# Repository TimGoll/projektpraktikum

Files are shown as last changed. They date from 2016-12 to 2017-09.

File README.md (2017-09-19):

# Dokumentation des Projektpraktikums
Projektpraktikum (Mikrocontrollerpraktikum + Messtechnikpraktikum) Winter- + Sommersemester 2016/17 am LMT

_Tim Goll, Matthias Baltes, Matthias Jost, Markus Herrmann-Wicklmayr_

## Aktuelle Demonstrationsvideos:
[Demovideo 1 (03.12.2016)](https://www.youtube.com/watch?v=2sz4_vMzZEc) <br>
[Demovideo 2 (04.06.2017)](https://www.youtube.com/watch?v=daKc67VaTdY)

## Verwendete Bibliotheken:
1. [**mThread**](http://www.kwartzlab.ca/2010/09/arduino-multi-threading-librar/): <br>
 Erstellt Pseudothreads auf dem Board, die nacheinander ausgeführt werden. Jeder Thread hat seine eigene ```loop()```. <br>
 Threads werden hinzugefügt mittels ```main_thread_list -> add_thread(CLASSNAME)```, anschließend laufen sie unbegrenzt weiter. **Hinweis:** Es sind anscheinend maximal 10 Threads möglich.

2. [**newdel**](https://github.com/jlamothe/newdel): <br>
 Fügt die Keywörter ```new``` und ```delete``` hinzu. Wird für mThread benötigt und musste leicht angepasst werden, damit sie auf neueren Arduino-Boards funktioniert.

3. [**QueueList**](http://playground.arduino.cc/Code/QueueList): <br>
 Fügt verkettete Listen hinzu, welche beliebige Datentypen speichern können. **Hinweis:** Es ist nicht möglich Pointer in ihnen zu speichern.

4. [**Adafruit BME280**](https://github.com/adafruit/Adafruit_BME280_Library) und [**Adafruit Sensor**](https://github.com/adafruit/Adafruit_Sensor): <br>
  Ansteuerung des Boschsensors (Die Version im Repo ist leicht verändert).

## Programmablauf:
1. Programm startet automatisch nach Herstellung der Stromversorgung.
2. Es kann ein Programm per USB von LabView übertragen werden, oder - falls eine SD-Karte eingesteckt ist - ein Programm von der SD-Karte aus gestartet werden.
3. Programm liest Daten (werden überprüft) und startet nach einem Tasterdruck/"Start"-Befehl.
4. Arbeitet Eventlisten ab, gibt Debug-Informationen aus, sofern über Schalter aktiviert, während der Laufzeit einstellbar.
5. Im Idle-Modus nach vollständiger Abarbeitung aller Events; nach Abschluss des Programms leuchtet eine LED und das Display leuchtet grün.
6. Zum Starten eines weiteren Programms muss das Board zurückgesetzt werden.
7. Es sind maximal 14.000 Events auf dem Board möglich. Dann ist der Speicher voll.
8. Für eine korrekte Steuerung muss **mindestens ein Ventil und ein MFC** existieren, sonst kommt es zu Fehlern. Falls in der Steuerung kein MFC/Ventil gebraucht wird, kann man auch einen leeres pseudo MFC/Ventil hinzufügen, das keine Events hat. Dafür muss nicht einmal Hardware angeschlossen sein.

## Übertragungsprotokoll (LabView -> Mikrocontroller):
Die Übertragung erfolgt zeilenweise in einem möglichst übertragungssicheren Format. Als Anfangs- und Endzeichen dienen zur Überprüfung der Vollständigkeit jeweils eine öffnende und eine schließende spitze Klammer. Alle Zeitangaben sind in Millisekunden. Es gibt nur ganzzahlige Integerwerte.

Die IDs der MFCs und Ventile ergeben sich jeweils aus der gegebenen Reihenfolge startend bei null.

**Zeilenweise Betrachtung der Übertragung**:

1. ```<Anzahl MFC, Anzahl Ventile>```
2. ```<Adresse MFC 0, Adresse MFC 1, ...>```
3. ```<Typ MFC 0, Typ MFC 1, ...>```
4. ```<Ventilplatinenadresse1, ...>``` Hexadezimale Ventilplatinenadressen
5. ```<Platinen-ID Ventil-Pin-ID, Platinen-ID Ventil-Pin-ID, ...>```
6. ```<Messintervall>``` Mess- und Speicherintervall in Millisekunden
7. ```<Datum + Zeit>``` Aktuelles Datum & Uhrzeit. Wird im Header der Messung gespeichert, relativ dazu wird gemessen
8. ```<begin>``` Ende des Headers, Beginn mit der Eventübertragung
9. ```<MFC oder Ventil, ID, Wert, Zeit>``` Setze Events. Hierbei müssen die Events je MFC/Ventil zeitlich sortiert sein, um eine einfachere Verarbeitung zu gewährleisten. Untereinander dürfen die Events jedoch vertauscht sein. (Zeit von MFC2 darf vor MFC1 sein, auch bei späterer Übertragung. Jedoch darf Zeit von MFC1 nicht vor der Zeit von MFC1 sein)
10. ```<end>``` Ende der Eventübertragung, warte auf Start der Messung
11. ```<start>``` Nicht zwingend notwendig, kann auch manuell per Taster gestartet werden

**Beispiel**:

```
<6,9>
<adresse0,adress1,adresse2,adresse3,adresse4,adresse5>
<typ0,typ1,typ2,typ3,typ4,typ5>
<0x20>
<0 0, 0 1, 0 2, 0 3, 0 4, 0 6, 0 9, 0 12, 0 15>
<10>
<08.02.2017-13:03:29>
<begin>
<M,0,120,1000>
<M,0,240,1500>
<M,1,170,800>
<M,0,150,1700>
...
<V,0,1,1200>
...
<end>
<start>
```

**Softwarereset**: Es ist auch möglich, das Board per Software neu zu starten. Dafür muss ein ```reset``` Befehl übertragen werden, woraufhin das Board neu startet und anschließend wieder ein ```ready``` ausgibt. (Hardwareimplementierung noch ausstehend). Weiteres siehe Ausblick.

## Serielle Kommunikation:
Vier Ports des Boards werden verwendet. Port 0 dient zur Kommunikation mit LabView (IN/OUT), Port 1 gibt Debug-Nachrichten aus, sofern der Debug-Schalter am Board aktiviert ist. Zur Kommunikation mit den MFCs dient Port 2.

Es gibt eine extra Klasse namens ```serialCommunication```, welche die Kommunikation über die vier Ports verwaltet. Zu Beginn muss in der ```setup()```-Funktion der Hauptino das Objekt initialisiert werden:
```cpp
srl->setSerial(&Serial1, &Serial3, &Serial2, &Serial4); //labview / debug / mks / buerkert
```
Anschließend kann man an beliebiger Stelle im Programm diese Klasse einfach nutzen:
```cpp
srl->print('D', "Hallo Welt!"); //(Typ: L, D, M, B / Ausgabetext)
srl->println('D', "Hallo Welt mit Zeilenende!"); //Natuerlich gibt es das ganze auch mit Linebreak
```
Der Typ der Ausgabe entscheidet, welcher Port genutzt wird. Hierbei gibt es drei Typen: L, D und M, B für LabView, Debug, MKS und Bürkert. Die Parameter, wie die Baudrate, werden in der **config.h** eingestellt.

Über den LabView-Port wird nach erfolgreicher Initialisierung des Boards ein _"ready"_ gesendet. Wurde ein Befehl korrekt erkannt und erfolgreich verarbeitet, wird ein _"ok"_ gesendet, andernfalls kommt ein Errorcode. Nach Abschluss einer Messung wird eine _"finished"_ Zeile übertragen.

## Serielle Hardware
Die Verbindung zwischen dem Teensy und dem PC über eine serielle Verbindung wird mit dem IC **CH340G** realisiert. Dieser funktioniert Plug and Play unter Windows (Windows 10 getestet) und lässt sich auch [mit einfachen Treibern](https://github.com/adrianmihalko/ch340g-ch34g-ch34x-mac-os-x-driver) unter MacOS zum Laufen bringen.

## SD Karte
Das SD-System des Teensy basiert auf FAT, daher sind Dateinamen maximal acht Zeichen lang (Großbuchstaben). Dateinamen, die länger als diese acht Zeichen sind, werden automatisch gekürzt (8.3 Format). Beim Speichern in eine Datei ist es jedoch wichtig, dass der Dateiname maximal 8 Zeichen hat, ansonsten tritt ein Fehler auf.

Die SD-Karte wird nur einmal beim Programmstart initialisiert. Es ist also nicht möglich, sie während der Laufzeit einzustecken oder zu entfernen. Ersteres wird nicht erkannt, letzteres führt zu Datenverlust. Wenn eine SD-Karte beim Programmstart erkannt wird, so wird dies durch ein Zeichen in der linken oberen Ecke gezeigt.

Eine neue SD-Karte kann einfach in den Leseslot gesteckt werden, alle nötigen Verzeichnisse werden automatisch erstellt. (Board muss resettet werden!)

### Messergebnisse
**Namensschema:** ```YYMMDDXX```<br>
Datum in Zweierschreibweise, zwei X für eine fortlaufende Nummerierung. Es sind maximal 100 (0..99) Messungen an einem Tag möglich. Falls der Zähler die 100 Überschreitet, werden kontinuierlich Messungen unter der Nummer _"xx"_ abgespeichert und überschrieben.

Beim Speichern auf der SD-Karte wird eine Datei mit einem Dateinamen, der das Datum und die Messungsnummer (falls mehrere Messungen pro Tag) enthält, erzeugt. Im gleichen Zuge wird in der txt-Datei ein Header in Klartext erstellt. Dieser enthält wesentliche Informationen wie die Startuhrzeit (diese stammt aus dem Header des Programms) der Messungen, die Anzahl der MFC's und Ventile, sowie die Typen der MFC's.

#### Beispielmessung
```
Messung am:     17.03.2017-22:12:46
Messintervall:  100
Anzahl Ventile: 6
Anzahl MFCs:    4
Typen der MFCs: MKS MKS MKS MKS

Wertsortierung: Laufzeit (ms), MFC Soll, MFC Ist, Ventil Soll, Bosch (Temp /C, Druck /Pa, Feucht /%)

0   0 0 0 0 0 0 0 0 0 0 0 0 0 0 22.520000 99050.312500 53.992188
100 0 0 0 0 0 0 0 0 0 0 0 0 0 0 22.520000 99050.312500 53.992188
200 0 0 0 0 0 0 0 0 0 0 0 0 0 0 22.520000 99048.062500 54.057617
300 0 0 0 0 0 0 0 0 0 0 0 0 0 0 22.520000 99042.750000 54.057617
.........
```

### Programme
1. Einzelne Befehlzeilen werden mit einem ```\n``` (Zeilenumbruch) voneinander getrennt.
2. Die Befehlszeilen werden bei Dateien **nicht** mit ```<``` und ```>``` umschlossen.
3. Leerzeilen und Leerzeichen werden ignoriert
4. Ebenso wird alles in einer Zeile nach einem ```#``` ignoriert, somit sind Kommentare möglich.
5. Dateinamen sind im FAT 8.3 Format und dürfen nicht mit ```.``` oder ```_``` beginnen.
6. Programme müssen sich im Ordner ```programs``` auf der SD Karte befinden.

#### Beispielprogramm
Nach dem Einstecken einer neuen SD Karte und dem Neustart des Boards wird eine Beispielprogrammdatei auf der SD Karte erstellt, die wie folgt aussieht:

```
# DIES IST EINE BEISPIELDATEI.
# Dateinmane duerfen nicht mit '.' oder '_' beginnen, sonst werden sie ignoriert.
# Im Gegensatz zu einer LabView Uebertragung sind hier Kommentare moeglich.
# leere Zeilen und Leerzeichen werden ignoriert.

4,16 #(MFCs, Ventile) in Dateien werden keine Tags benutzt
01,21,07,14 #(MFC Adressen)
Buerkert,Buerkert,MKS,MKS #(MFC Typen)
0x20 #(Ventilplatinen Adressen)
0 0, 0 1, 0 2, 0 3, 0 4, 0 5, 0 6, 0 7, 0 8, 0 9, 0 10, 0 11, 0 12, 0 13, 0 14, 0 15 #(Ventil Pins)
250 #(Messintervall)
08.02.2017-13:03:29 #(Datumstring)

begin #Ende Header, uebertrage Eventliste

M,0,120,1000
V,0,1,1000
V,1,1,750

end #Uebertragung abgeschlossen
start #Optionaler automatischer Programmstart
```

## I2C
I2C wird als Hauptkommunikationsbus verwendet. Folgende Adressen sind belegt (In der Klammer stehen die alternativen Adressen):
- Display: 0x38 (--)
- BME280: 0x76 (0x77)
- IO Expander (Ventilplatine, PCA9555): 0x20 (0x21 .. 0x27)

## BME280
Der Boschsensor wird innerhalb der Klasse ```main_boschCom``` verwaltet. Dort wird ein bme-Objekt erstellt. Dieses Objekt wird geliefert von einer leicht angepassten Adafruit-Bibliothek. (Diese könnte man noch weiter reduzieren, da der ganze SPI Bereich eigentlich nicht gebraucht wird)

**Anschluss des Sensors:**<br>
Folgende Pinbelegung ergab sich nach einigem Durchmessen mit einem Multimeter. Bisher erwies sich dieses Layout als korrekt.
```
        +----\_/----+
    VDD |o         o|                     VDD und VDDIO   : 3V3
  VDDIO |o         o|                     GND             : 0V
    GND |o         o|                     SDO (Adresspin) : 0V (0x76), 3V3 (0x77)
    SDO |o         o|                     CSB             : 3V3
    SDA |o         o|                     SDA / SCL       : I2C Bus (3V3 level)
    SCL |o         o|
    CSB |o   |_|   o|
        |o         o|
        |o         o|
        |o         o|
        |o         o| (SCL)
        |o         o| (SDA)
        |o         o|
        |o         o|
        |           |
        +-----------+
```
Den Sensor auslesen kann man in der besagten ```main_boschCom``` mit folgenden Befehlen:
```cpp
this->bme280->readTemperature();
this->bme280->readPressure();
this->bme280->readHumidity();
```

## Ventile
Die Ventilsteuerung befindet sich auf einer eigenen Platine. Das hat die beiden Vorteile, dass zum einen Kurzschlüsse auf der Ventilplatine keinen Schaden an der Hauptsteuerung verursachen können und es zum anderen möglich ist, "beliebig" viele Ventile mit einem Mikrocontroller zu steuern.

Theoretisch sind bis zu 8 Ventilplatinen mit je 16 Ventilen möglich, also insgesamt 128 Ventile. Auf der Platine befindet sich ein dreipoliger DIP-Switch zum Einstellen der Adresse (Adressraum: 0x20..0x27). Die Adressen sind bei Programmstart per LabView an den Controller zu übertragen. Jede der acht Platinen hat 16 Pins (0 bis 15), die auch bei der Initialisierung so angegeben werden müssen (```<Platinen-ID Pin-ID, ...>```). Intern haben die Ventile jedoch eine andere, fortlaufende, Nummerierung (siehe Übertragungsprotokoll).

Die softwareseitige Ansteuerung wird mittels einer kleinen von uns geschriebenen Bibliothek namens ```pca9555``` (Name des I2C ICs) realisiert. Angelehnt an die Syntax der Arduino-Umgebung gibt es auch hier eine ```digitalWrite(pinNumber)```-Funktion, der Einfachheit halber haben wir jedoch auf weitere Funktionen verzichtet und bei Porgammstart werden automatisch alle Pins als Ausgang definiert.

## Display:
Das Display ist via I2C mit dem Board verbunden, die Hintergrundbeleuchtung funktioniert mittels drei PWM Anschlüssen, einer für jede Grundfarbe. Daraus können beliebige Hintergrundfarben erzeugt werden. <br>
Je nach Meldungstyp ist die Hintergrundfarbe unterschiedlich. Folgende Typen gibt es:

- **Unkritische Fehler**: Error Code Level 1000; Dies sind Fehler, die beispielsweise bei der Kommunikation auftreten, aber keinen Programmabbruch benötigen. Sie werden auf dem Display für 2 Sekunden angezeigt. Farbe: _orange_
- **Kritische Fehler**: Error Code Level 5000; Diese Fehler führen zu einem Abbruch des Programms und werden auf dem Display angezeigt bis der Fehler behoben wurde. Farbe: _rot_

Standardmäßig werden auf dem Display aktuelle Daten zum Programmstatus angezeigt.

**Beispielanzeige**:
```
STANDARD:                      ERRORBEISPIEL:                 ENDANZEIGE:
+----------------------+       +----------------------+       +----------------------+
|          #M:04 #V:07 |       |      ERROR 1001      |       |          #M:04 #V:07 |
|                      |       |                      |       |                      |
| LAUFZEIT:00:01:34:17 |       |       Falscher       |       |    ABGESCHLOSSEN     |
| V03-0001-00:01:16:22 |       |     Zeilenbeginn     |       |     02:05:24:34      |
+----------------------+       +----------------------+       +----------------------+
Hintergrund: weiß              Hintergrund: organge/rot       Hintergrund: grün
```

- **Standardanzeige:** <br>
 Zeile 1: Anzahl MFCs und Anzahl Ventile <br>
 Zeile 2: xxx <br>
 Zeile 3: Laufzeit der Software, relativ zum Messstart <br>
 Zeile 4: Letztes Event, Typ-ID-Wert-Zeit
- **Erroranzeige:** <br>
 Zeile 1: Error ID <br>
 Zeile 2: xxx <br>
 Zeile 3+4: Kurzbeschreibung des aufgetretenen Fehlers
- **Endanzeige:** <br>
 Zeigt durchgängig diesen Text an, lässt sich nur zurücksetzen durch Reset des Boards

## Errormeldungen:
Bei allen Fehlermeldungen im 1000er Bereich wird das Programm weiterhin ausgeführt, es wird jedoch eine Wiederholung der entsprechenden Zeile erwartet, daher sind diese Codes LabView-seitig abzufangen.

### 1000:
**Maximale Input-String Länge überschritten.** In der _config.h_ wird eine Zeichenanzahl definiert, die pro Zeile gesendet werden darf. Diese Länge darf nicht überschritten werden.

### 1001:
**Falscher Zeilenbeginn.** Die Zeile muss mit einer öffnenden spitzen Klammer ```<``` begonnen werden, damit sie als gültig akzeptiert wird. Dies dient der Vollständigkeitsüberprüfung.

### 1002:
**Falsches Zeilenende.** Die Zeile muss mit einer schließenden spitzen Klammer ```>``` beendet werden, damit sie als gültig akzeptiert wird. Dabei darf man jedoch nicht vergessen, dass die Stringeingabe mit einem Zeilenumbruch ```\n``` als vollständig markiert wird. Dies dient der Vollständigkeitsüberprüfung.

### 1003:
**Lese-Timeout überschritten.** In der _config.h_ wird eine maximale Lesezeit pro String definiert. Wird diese Zeit überschritten, wird das Lesen des Strings an dieser Stelle abgebrochen.

### 1004:
**Falsche Anzahl an Argumenten.** Bei der Übertragung von LabView an den Controller wird immer überprüft, ob die Anzahl an eingetroffenen Elementen der Anzahl an erwarteten Elementen entspricht.

### 5000:
**Zugriff auf nicht definierte MFC/Ventil ID.** Tritt dieser Fall ein, dann wird eine irreversible Errormeldung geworfen, die nur duch einen Programmneustart behoben werden kann. Man sollte in diesem Fall seine Eingaben darauf überprüfen, ob in den Events nur auf vorher definierte MFCs/Ventile zugegriffen wird.

## MFCs
Bei unserem Aufbau verwenden wir zwei verschiedene Typen von MFCs. **Bürkert** und **MKS** sind die beiden Hersteller. Dazu gibt es noch alte analoge MFCs, die von einer anderen Projektgruppe digitalisiert wurden. Diese basieren dadurch auch auf dem **Bürkert** Protokoll. <br>
Von uns angesteuert werden alle MFCs von ihrer jeweiligen Klasse, je nach Typ bekommen sie bei der Initialisierung jedoch ein anderes Kommunikationsobjekt übergeben. Dieses Objekt führt verschiedene Befehle aus und gibt gegebenenfalls Daten an das MFC-Objekt zurück.

Um Verzögerungen zu verringern wird die Übertragung mittels zeitlichen Interrupts gesteuert. Sowohl mfcCom_mks, als auch mfcCom_buerkert besitzen einen ```IntervalTimer```, der mikrosekundengenaue Callbackfunktionen ausführen kann. Zum Start der Befehlsübertragung wird die Übertragungs- und Antwortzeit berechnet, sowie die erwartete Pause zwischen den beiden Übertragungen. Nach dem Schieben des Strings in den seriellen Outputbuffer wird ein Interrupt auf den Augenblick nach der Übertragung gesetzt . Die aufgerufene Funktion setzt den Enablepin des RS-485 IC und einen weiteren Interrupt auf den erwarteten Zeitpunkt nach dem kompletten Eintreffen der Antwort. Anschließend wird der empfangene Wert der Antwort in einem vorher gesetzten Pointer gespeichert und der Port wieder freigegeben. Es gibt einen Lesetimeout, der in der _config.h_ eingestellt werden kann. <br>
Während einer Übertagung (Befehl senden und Antwort erhalten) ist der Port gesperrt und weitere Befehle werden zurückgewiesen. Unsere Steuerung registriert dies aber und sendet den Befehl anschließend erneut.

### Bürkert [[Handbuch]](../master/dokus/MA8006-Supplem.MFC-DE-DE.pdf)
Hier sind die für uns relevanten Informationen herausgeschrieben, siehe Seite 8ff.
```
Präampel:       2..20 mal 0xFF          // Synchronisierung des Datenverkehrs
Startzeichen:   Master->Slave 0x02      // WAS?
                Slave->Master 0x06      // WAS? Definiert dies, ob eine Antwort erwartet wird?
Adresse:        BIT 7:    1             // unser Master ist Primär
                BIT 6:    0             // kein Burstmodus Hier
                BIT 5..0: 0..32         // Pollingadresse
Befehl:         8-bit Zahl
                ohne 31, 127, 254, 255
Bytezählwert:   Anzahl der Antwortbytes + Datenbytes
Antwortcode:    Nur für Slave->Master (2 Byte groß)
Daten:          Hängen von Befehl ab
Checksumme:     8-bit XOR Kombination von Startzeichen bis Daten
```
Befehle:
```
0x03 - ReadCurrentAndFourDynamicVariables (S.14)
0x92 - ExtSetpoint (S.18)
```
Flusseinheit in Prozent. Maximal 40,976sccm.

### MKS [[Handbuch]](../master/dokus//120115/MF1-man.pdf)
"Human Readable Protocol" siehe Seite 73ff, Übertragung vollständig in ASCII Zeichen.
```
Präambel:       @ (Synchronisierung des Datenverkehrs)
Adresse:        2 Byte, 00 bis 99?
Befehl:         1-stelliger Befehlscode (S.74)
Wert:           1.00000 (Beispielhaft, aber diese Bytegröße (7))
Terminierung:   \r (Carriage Return)
```
Befehle:
```
F  - Lese aktuellen Fluss (S.74)
S  - Setze Fluss (S.74)
```
Fluss: 0..500 sccm (S.16)

Flusseinheit in sccm (cm^3/min)

## Programmaufbau:
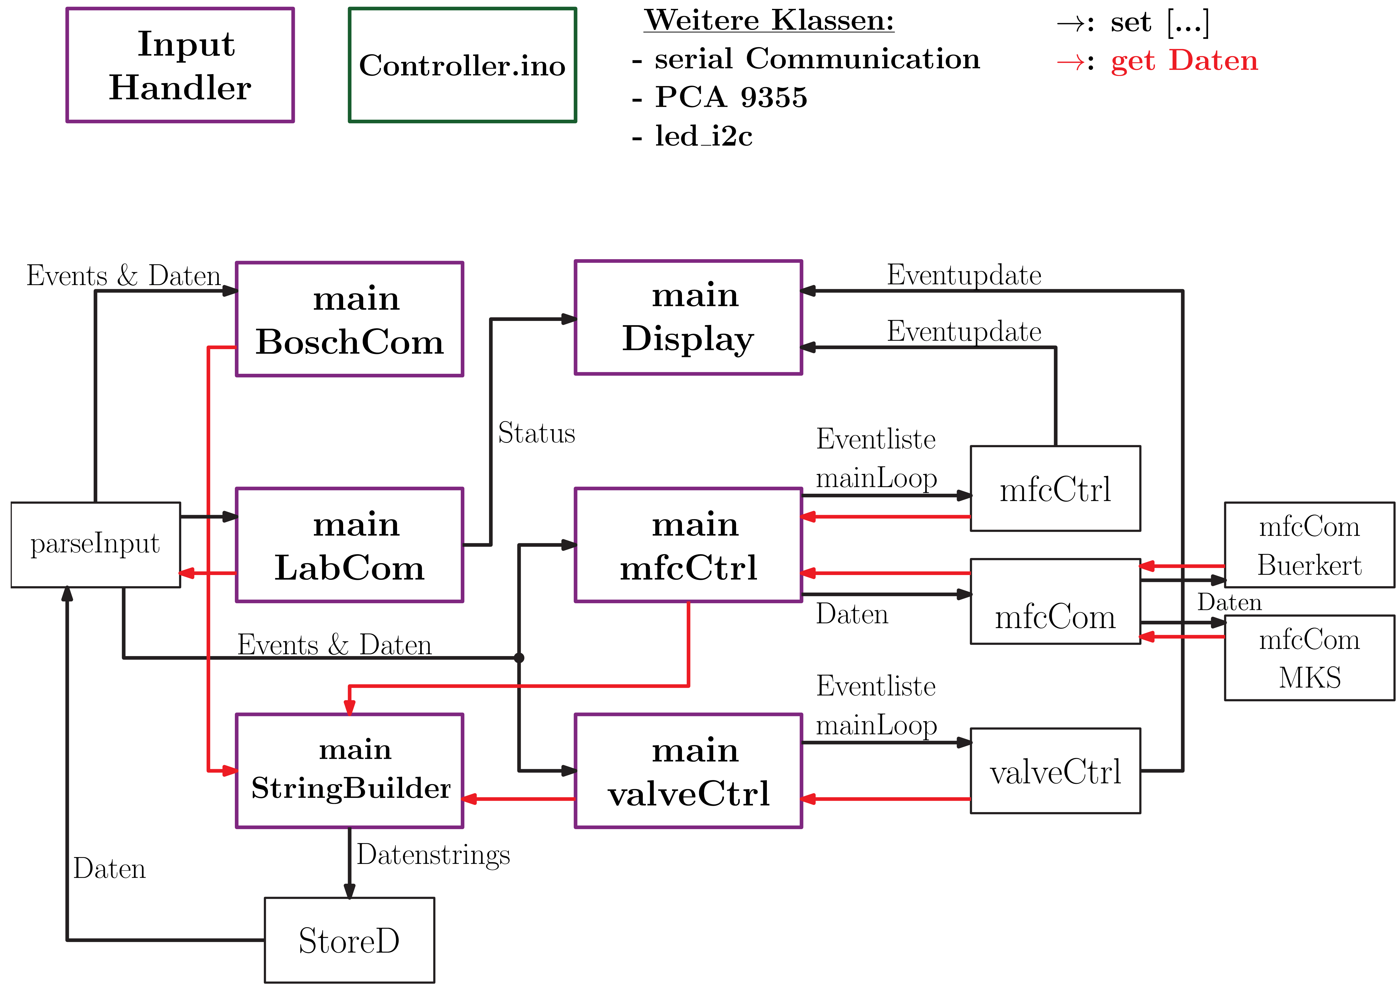
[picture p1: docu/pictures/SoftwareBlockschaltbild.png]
Blockschaltbild

_**Blockschaltbild der Software.** Violette Klassen stellen Hauptklassen mit eigenem Thread dar._

### Hauptdatei:
1. **Controller.ino**: [[ino]](../master/controller/controller.ino) <br>
 Hier werden die Hauptobjekte erstellt und verwaltet. Außerdem werden an dieser Stelle die Threads gestartet und später auch wieder gestoppt. Vor dem Start der Threads werden noch Adressen zwischen den einzelnen Objekten ausgetauscht (beispielsweise die der Queues zum späteren Datenaustausch).

### Hauptklassen:
Aus allen Klassen mit einem "main" im Namen wird immer nur **ein** Objekt abgeleitet. Außerdem besitzen sie eine ```loop()```-Funktion, da die Klasse in Pseudothreads ausgeführt werden.

1. **main_labCom** [[cpp]](../master/controller/src/main_labCom.cpp) [[h]](../master/controller/src/main_labCom.h): <br>
Quasi Hauptklasse des Programms, verwaltet die Kommunikation mit LabView.

2. **main_boschCom** [[cpp]](../master/controller/src/main_boschCom.cpp) [[h]](../master/controller/src/main_boschCom.h): <br>
 Liest getaktet den Boschsensor aus und speichert die Werte.
3. **main_stringBuilder** [[cpp]](../master/controller/src/main_stringBuilder.cpp) [[h]](../master/controller/src/main_stringBuilder.h): <br>
 Dieses Objekt sammelt sich per Abfragen alle Daten, die in der Ausgabe gebraucht werden, zusammen und baut im Messtakt daraus Strings, welche an LabCom und StoreD weiter gegeben werden. Diese Klasse erzeugt und verwaltet StoreD.

4. **main_mfcCtrl** [[cpp]](../master/controller/src/main_mfcCtrl.cpp) [[h]](../master/controller/src/main_mfcCtrl.h): <br>
 Verwaltet alle mfcCtrl Objekte.

5. **main_valveCtrl** [[cpp]](../master/controller/src/main_valveCtrl.cpp) [[h]](../master/controller/src/main_valveCtrl.h): <br>
 Verwaltet alle valveCtrl Objekte.

6. **main_display** [[cpp]](../master/controller/src/main_display.cpp) [[h]](../master/controller/src/main_display.h): <br>
 Verwaltet die Displaybefehle und baut Anzeigen anhand von Daten.

### Nebenklassen:
1. **mfcCtrl** [[cpp]](../master/controller/src/mfcCtrl.cpp) [[h]](../master/controller/src/mfcCtrl.h): <br>
 Verwaltung eines einzelnen MFCs.
2. **valveCtrl** [[cpp]](../master/controller/src/valveCtrl.cpp) [[h]](../master/controller/src/valveCtrl.h): <br>
 Verwaltung eines einzelnen Ventils.
3. **mfcCom** [[cpp]](../master/controller/src/mfcCom.cpp) [[h]](../master/controller/src/mfcCom.h): <br>
 Serielle Kommunikationsverwaltung der MFCs.
4. **mfcCom_buerkert** [[cpp]](../master/controller/src/mfcCom_buerkert.cpp) [[h]](../master/controller/src/mfcCom_buerkert.h): <br>
 Serielle Kommunikation mit Bürkert MFCs.
5. **mfcCom_mks** [[cpp]](../master/controller/src/mfcCom_mks.cpp) [[h]](../master/controller/src/mfcCom_mks.h): <br>
 Serielle Kommunikation mit MKS MFCs.
6. **StoreD** [[cpp]](../master/controller/src/StoreD.cpp) [[h]](../master/controller/src/StoreD.h): <br>
 Sorgt dafür, dass Daten auf der SD-Karte gespeichert/gelesen werden.
7. **parseInput** [[cpp]](../master/controller/src/parseInput.cpp) [[h]](../master/controller/src/parseInput.h): <br>
 Zerteilt die Befehlsstrings von LabView und der SD-Karte.

### Eigene Bibliotheken
1. **serialCommunication** [[cpp]](../master/controller/src/ownlibs/serialCommunication.cpp) [[h]](../master/controller/src/ownlibs/serialCommunication.h): <br>
 Überklasse zu Arduino Serial. Verteilt Eingaben anhand der Parameter automatisch auf die verschiendenen seriellen Ports, die sich auch dort komplett deaktivieren lassen.
2. **inputHandler** [[cpp]](../master/controller/src/ownlibs/inputHandler.cpp) [[h]](../master/controller/src/ownlibs/inputHandler.h): <br>
 Kümmert sich um Tastereingaben, ruft Callbackfunktionen auf. Entprellt und erkennt Flanken. <br>
 Ermöglicht außerdem Dauerpulse zu senden, indem man zwei weitere Werte im Aufruf hinzufügt. Die Klasse initialisiert den entsprechenden Button dann automatisch.
 ```cpp
 inputHandler->addInterrupt(PIN_ID, FUNCTION, BUTTON_STATE);
 inputHandler->addInterrupt(PIN_ID, FUNCTION, BUTTON_STATE, MIN_PRESS_TIME, PUSH_INTERVAL);
 ```
3. **lcd_I2C** [[cpp]](../master/controller/src/ownlibs/lcd_I2C.cpp) [[h]](../master/controller/src/ownlibs/lcd_I2C.h): <br>
 Steuert das Display an.
4. **pca9555** [[cpp]](../master/controller/src/ownlibs/pca9555.cpp) [[h]](../master/controller/src/ownlibs/pca9555.h): <br>
 Steuert die Ventilplatine via I2C an.

### Sonstige:
1. **common** [[cpp]](../master/controller/src/ownlibs/common.cpp) [[h]](../master/controller/src/ownlibs/common.h): <br>
 Standardfunktionen, die überall gebraucht werden (```trim()```, ```getTimeString(time, timeString)```, ...).

2. **config** [[h]](../master/controller/src/config.h): <br>
 Einstellmöglichkeiten diverser Parameter. Eine Erläuterung dieser findet sich in der Datei selber.

3. **eventElement** [[h]](../master/controller/src/eventElement.h): <br>
 Event-Struct, welches von MFCs und Ventilen verwendet wird.

3. **errors** [[cpp]](../master/controller/src/errors.cpp) [[h]](../master/controller/src/errors.h): <br>
 Char-Array, in welchem die Displayausgaben der einzelnen Errormeldungen gespeichert sind.

## Testskript [[py]](../master/serial_connector_script/serial_connection.py)
Derzeit gibt es ein kleines Testskript zum Test der Steuerungssoftware auf dem Board. Bei der Ausführung ist zu beachten, dass keine andere serielle Verbindung geöffnet sein darf (Arduino-Debug-Monitor, ...).

Zur Ausführung müssen ```Python 2.7``` und ```pySerial``` installiert sein und bestenfalls die PATH-Variable für die Konsole gesetzt sein. Da das Programm hardgecoded ist, muss der Port in Zeile 10 angepasst werden. Der Port ist beispielsweise in der Arduino IDE sehr einfach einzusehen.

Ist alles vorbereitet, wird das Skript mit ```python serial_connection.py``` ausgeführt, insofern man sich im Verzeichnis dieser Datei befindet. In der Datei kann in einem Array die Übertragung definiert werden.

[[Einrichtung von Python (Windows)]](https://learn.adafruit.com/arduino-lesson-17-email-sending-movement-detector/installing-python-and-pyserial)

## LabView:
Das LabVIEW Programm erstellt beim Start eine serielle Verbindung mit dem Teensy-Board. Dazu müssen die Baudrate und der richtige Port eingestellt werden. Nachdem die Verbindung erstellt wurde, wartet LabVIEW auf ein Ready vom Teensy-Board.
Wenn ein ```ready``` gelesen wurde beginnt die Übertragung des Headers. Hier wird Zeile für Zeile, wie vorher im
Übertragungsprotokoll beschrieben, gesendet. Nach jeder Zeile wartet LabVIEW auf die Überprüfung des Teensy-Boards. Wenn ein ```ok``` zurückkommt, fährt das Programm mit der nächsten Zeile fort.
Bei einem 1000er Error wird die letzte Zeile erneut gesendet bei einem 5000er Error wird die Übertragung abgebrochen (siehe Error Bibliothek).
Nach dem Header werden die einzelnen Werte, analog zum Header, Zeile für Zeile mit Überprüfung gesendet.

Der Header und die einzelnen zugehörigen Werte werden als zwei Tabellen eingegeben.

In Zeile 1 des Headers steht, ob es sich um ein Mfc oder Ventil handelt. <br>
In Zeile 2 wird die ID zugewiesen, die für den späteren Ablauf wichtig ist (Die Steuerung auf dem Board macht die ID-Zuweisung automatisch). <br>
In Zeile 3 steht die Adresse und in Zeile 4 der Typ des Mfcs. <br>

Zusätlich zu den 2 Tabellen hat das LabVIEW Programm noch eine Eingabe für die Anzahl der Ventilplatinen und der Messauflösung.

Input-String in Datumsobjekt: ```%d.%m.%Y-%H.%M.%S```

**Verwendete Treiber:** NI-VISA Treiber

## Elektronik:
### Pinbelegung Teensy
Untenstehend eine Zeichnung des Teensyboards mit allen Anschlüssen und unserer aktuellen Belegung.
```
                                         U
                                +------| S |------+
                                |o GND |_B_| VIN o|
                  Labview - RX1 |o 00        GND o|
                  LabView - TX1 |o 01        3V3 o|
                                |o 02         23 o| AUSGANG - Software Reset
                                |o 03         22 o|
                                |o 04         21 o|
                                |o 05         20 o| EINGANG - Debug-Schalter
            Debug-LED - AUSGANG |o 06         19 o| I2C - SCL0
                    Debug - RX3 |o 07         18 o| I2C - SDA0
                    Debug - TX3 |o 08         17 o|
                 Uart-MKS - RX2 |o 09         16 o| EINGANG - OK-Taster
                 Uart-MKS - TX2 |o 10         15 o| EINGANG - Runter-Taster
                                |o 11         14 o| EINGANG - Hoch-Taster
                                |o 12         13 o| AUSGANG - Abgeschlossen-LED
                                |o 3V3       GND o|
                                |o 24            o|
                                |o 25            o|
           Enable MKS - AUSGANG |o 26         39 o|
       Enable Bürkert - AUSGANG |o 27         38 o|
                                |o 28         37 o| PWM - Displaybeleuchtung rot
                                |o 29         36 o| PWM - Displaybeleuchtung grün
                                |o 30  _____  35 o| PWM - Displaybeleuchtung blau
             Uart-Bürkert - RX4 |o 31 |  S  | 34 o|
             Uart-Bürkert - TX4 |o 32 |  D  | 33 o|
                                +-----------------+
```
### Pinbelegung Display
```
        +---+
  PWM_1 |o  |18                     
  PWM_2 |o  |                     
  PWM_3 |o  |                     
 5V_LED |o  |                     
  I/O_3 |o  |                      
  I/O_2 |o  |
  I/O_1 |o  |
  I/O_0 |o  |
        |o  |
        |o  |
        |o  |
        |o  |
  I/O_4 |o  |
  I/O_5 |o  |
  I/O_6 |o  |
   Poti |o  |
V_IN_5V |o  |
    GND |o  |1
        +---+
```
### Hardware
#### 1. Schaltskizze [[link]](../master/electronic/Schaltplan.pdf) <br>
#### 2. Gesamtübersicht
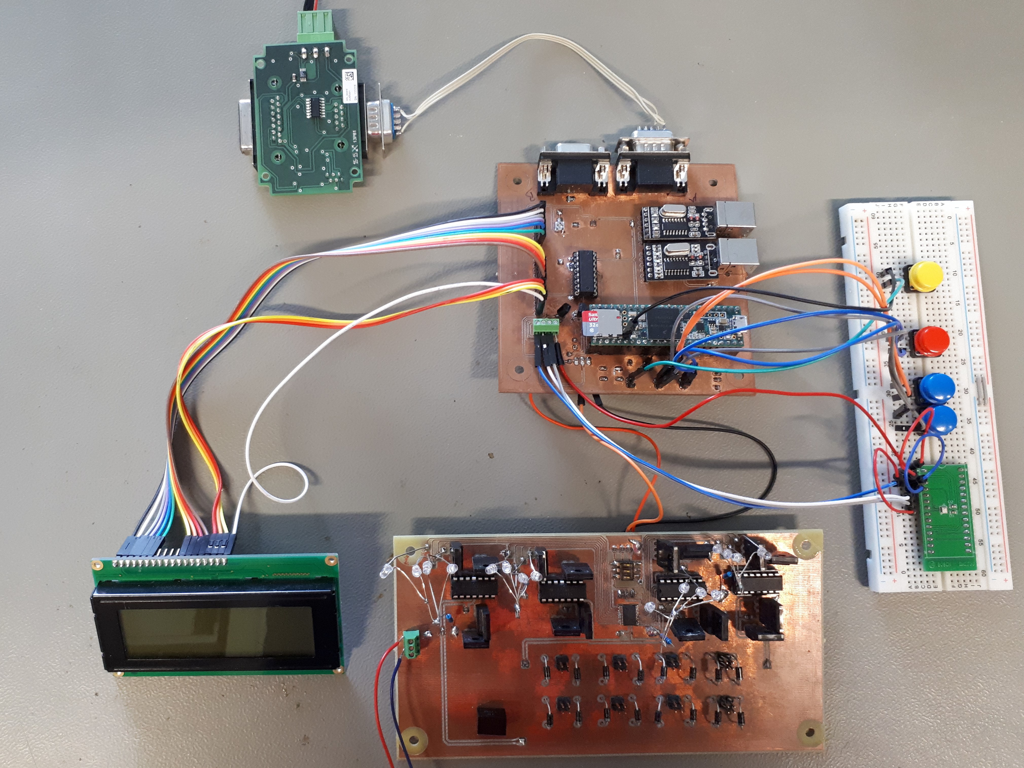
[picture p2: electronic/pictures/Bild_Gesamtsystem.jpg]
Gesamtübersicht


#### 3. Anschluss

* **Stromversorgung Control-Board, Valve-Board** <br>
  Die Stromversorgung des Control-Board erfolgt über die USB Ports.
  Die 5V und GND Leitungen von Debug Port und LabView Port sind auf der Platine zusammengeführt.
  Um eine stabile Stromversorgung zu gewährleisten, muss ein aktiver USB-Hub zwischen der Platine und dem Computer geschaltet werden,
  da sich die Platine nicht als USB-Verbraucher anmeldet und nur bis maximal 100mA über einen normalen USB Port erhält. <br>
  <br>
  Das Valve-Board muss an eine externe Spannungsversorgung angeschlossen werden, die 24V für die Ventile liefert. Auf der Platine werden   die benötigten 5V für den Multiplexer durch einen Regler erzeugt (siehe auch Bauteile Valve-Board).

* **Control-Board <-> Valve-Board** <br>
  Die Kommunikation zwischen den beiden Platinen erfolgt über I2C. Der Multiplexer auf dem Valve-Board arbeitet mit einem 5V Pegel.       Daher werden die Signalleitungen zunächst über einen Pegelwandler von 3V3 auf 5V gewandelt. Die Signalleitungen, sowie ein gemeinsames   GND Potential können am Control-Board an dem 3-poligen Anschlussblock oberhalb des Teensy Boards abgegriffen werden.
  Beginnend auf der dem Teensy näheren Seite: GND, SDA, SCL.

* **Control-Board <-> Bosch-Sensor** <br>
  Der Bosch Sensor wird an dem vier- poligen Anschlussblock links neben der Teensy Platine angeschlossen. Die Kommunikation erfolgt wie   beim Valve-Board über I2C. Außerdem werden eine GND und eine 3V3 Leitung benötigt.
  Beginnend auf der dem Teensy näheren Seite: 3V3, SCL, SDA, GND.

* **Control Board <-> MFC** <br>
  Die MFC's empfangen Daten nach dem RS485 Protokoll. Daher muss das TTL 3V3 Signal des Teensy zunächst umgewandelt werden (siehe         Hardware Control-Board).
  Um Verwechslungen auszuschließen werden die MFC's der Marke **Bürkert mit male D-Sub** angeschlossen. Die MFC's von **MKS mit female     D-Sub**. <br>

  Anschlussbelegung Bürkert auf Seite 7 im Datenblatt
  [[link]](../master/docu/data_sheets/bürkert_mfc.pdf) <br>
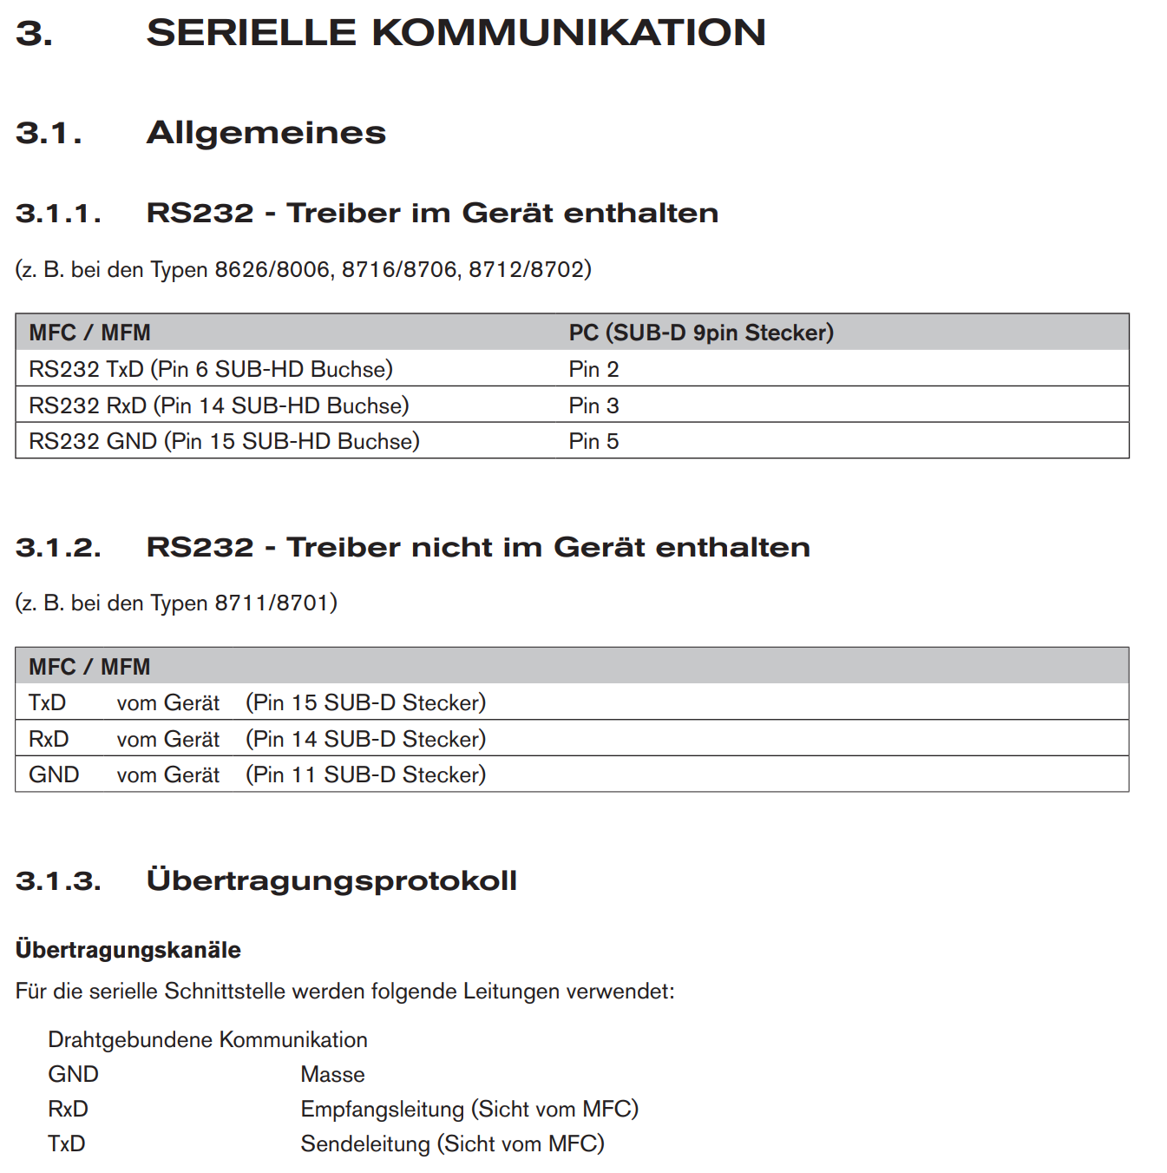
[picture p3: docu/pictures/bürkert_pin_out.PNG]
Bürkert Datenblatt Seite 4
  
  <br>
  <br>
  Anschlussbelegung MKS auf Seite 68 im Datenblatt (RTS Pin wird nicht verwendet)
  [[link]](../master/docu/data_sheets/mks_mfc.pdf) <br>
  Screenshost S.68

* **Control Board <-> LabView** <br>
  LabView kommuniziert mit dem Control-Board über den oberen, näher am Teensy gelegenen USB-B Anschluss.

*  **Control Board <-> Debug** <br>
   Der untere USB-B Anschluss sendet, sofern aktiviert, debugging Informationen. Um diesen USB Port zu aktivieren muss ein Schalter        auf der Platine umgelegt werden. Dieser ist als einzelner DIP-Switch ausgeführt und befindet sich über dem Teensy-Board.

*  **Control Board <-> Programmierung** <br>
   Um ein Programm auf das Teensy Board zu übertragen wird der Standarmäßige Micro-USB Port am Teensy selbst verwendet.

#### 4. Hardware Control-Board

 * **Teensy 3.6**
  Board [[link]](http://www.pjrc.com/teensy/) <br>
  Vorderseite [[link]](../master/docu/data_sheets/teensy_front.pdf) <br>
  Rückseite [[link]](./master/docu/data_sheets/teensy_back.pdf)

 * **20x4 LCD Display (RGB Backlight)**
  [[link]](https://www.adafruit.com/product/499) <br>
  Display Datasheet [[link]](../master/docu/data_sheets/display.pdf) <br>
  Display Controller HD44780U Datasheet [[link]](../master/docu/data_sheets/display_controller_HD44780U.pdf) <br>
  I2C-Chip für Display (PCF8574) [[link]](../master/docu/data_sheets/display_i2c_pcf8574.pdf)

 * **"TTL" (3V3) auf RS-485 - MAX14776E**
 [[link]](../master/docu/data_sheets/mfc_communication.pdf) <br>
 Der MAX14776E kann, bei 5V Versorungsspannung, sowohl 3V3 als auch 5V Pegel als High erkennen.

 * **UART <-> USB - CH340G**
  [[link]](../master/docu/data_sheets/usb_uart_interface_ch340g.pdf) <br>
  Auf dem Control-Board ist eine integrierte Variante des IC's verbaut: <br>
  [[link]](http://www.ebay.de/itm/252960740317)

 #### 5. Hardware Valve-Board
  * **I2C-Multiplexer - PCA9555**
   [[link]](../master/docu/data_sheets/valve_I2C_PCA9555.pdf) <br>

  * **Operationsverstärker - LMC6484**
   [[link]](../master/docu/data_sheets/valve_op-amp_lmc6484.pdf) <br>

  * **Transistoren -  IRFIZ24NPBF**
   [[link]](../master/docu/data_sheets/valve_transistor.pdf) <br>
  Bestellnummer bei Farnell: 9264388

  * **Pegelwandler - TSR 1 - 2450**
   [[link]](../master/docu/data_sheets/valve_tsr1-2450.pdf) <br>

 #### 6. LED-Anzeigen
 * **Control-Board**
   Power-LED über dem Lab-Vies USB Port. <br>
   Debug-LED neben dem Debug DIP-Schalter. <br>

 * **Control-Board**
   Jedes Ventil hat eine eigene LED, die leuchtet, wenn das Ventil geöffnet wird.

## Ausblick:
### RTC
Aktuell wird das Datum und die Uhrzeit von LabView aus übertragen. Insbesondere bei Messungen von der SD Karte ist dies jedoch eher unpraktisch. Man könnte daher den Datumstring (in parseInput) mithilfe einer RTC bilden. Da schon eine RTC inklusive Quarz auf dem Teensy verbaut ist, muss man nur eine Knopfbatterie an entsprechende Pins anschließen, um dieses Feature zu nutzen.

### Software Reset via 'reset' Befehl
Wenn per LabView der Befehl "reset" kommt, dann wird ein Pin auf HIGH gezogen, wodurch ein Transistor (evtl mit Kondensator) zu Ground durchschaltet und damit den Reset-Pin auf Ground zieht. Dies hat den Vorteil, dass das Board von LabView aus neu gestartet werden kann, wodurch alle Parameter zurück gesetzt werden. <br>
Dieses Feature ist softwareseitig bereits implementiert.

### Kommunikationscontroller
Aktuell haben wir einige Timingprobleme mit der seriellen Kommunikation des Teensyboards, da wir das Programm blockieren müssen, bis Daten gesendet sind und eine Antwort erhalten wurde. Sinnvoller wäre es, einen weiteren Microcontroller (beispielsweise einen Arduino Nano) zuzuschalten, welcher per SPI (sehr schnell) mit dem Teensy kommuniziert und die serielle Steuerung abarbeitet. Dadurch treten keine Verzögerungen mehr auf dem Hauptcontroller auf.

## Sonstiges:
1. **MarkdownGuide** [[link]](https://github.com/adam-p/markdown-here/wiki/Markdown-Cheatsheet)
2. **cloc-1.70.exe** [[link]](https://github.com/AlDanial/cloc)

 Ein kleines Programm zur Ausführung in der Konsole, welches den Softwareumfang darstellt. Wird wie folgt benutzt: ```prompt> cloc-1.70.exe controller/src``` (Auszuführen im Basepath des Projektes, dort liegt auch die exe)

 Ergibt folgendes:
 ```
 prompt> cloc-1.70.exe controller/src
       24 text files.
       24 unique files.
        2 files ignored.

 https://github.com/AlDanial/cloc v 1.70  T=0.50 s (80.0 files/s, 7966.0 lines/s)
 -------------------------------------------------------------------------------
 Language                     files          blank        comment           code
 -------------------------------------------------------------------------------
 C++                             19            530            220           2149
 C/C++ Header                    21            189            207            770
 -------------------------------------------------------------------------------
 SUM:                            40            719            427           2919  ==>  4065 lines
 -------------------------------------------------------------------------------
 ```

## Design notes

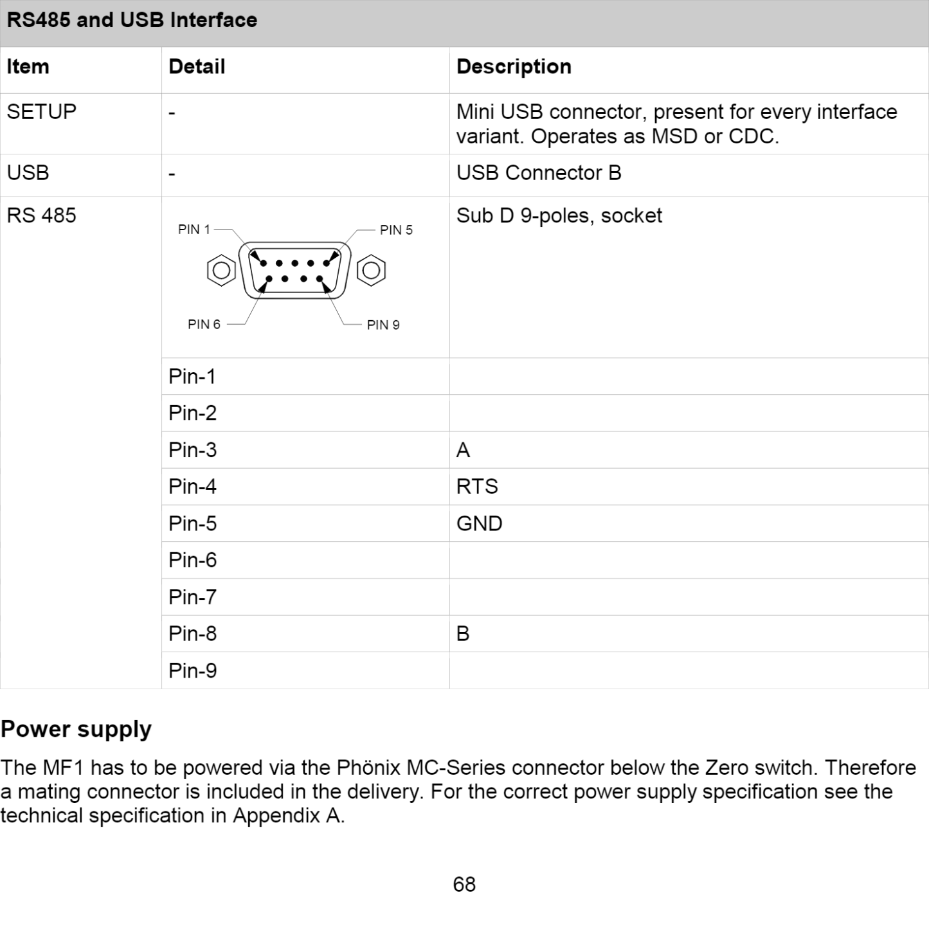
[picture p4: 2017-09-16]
docu/pictures/mks_pin_out.PNG

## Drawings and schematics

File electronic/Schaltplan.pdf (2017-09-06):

# Schaltskizze

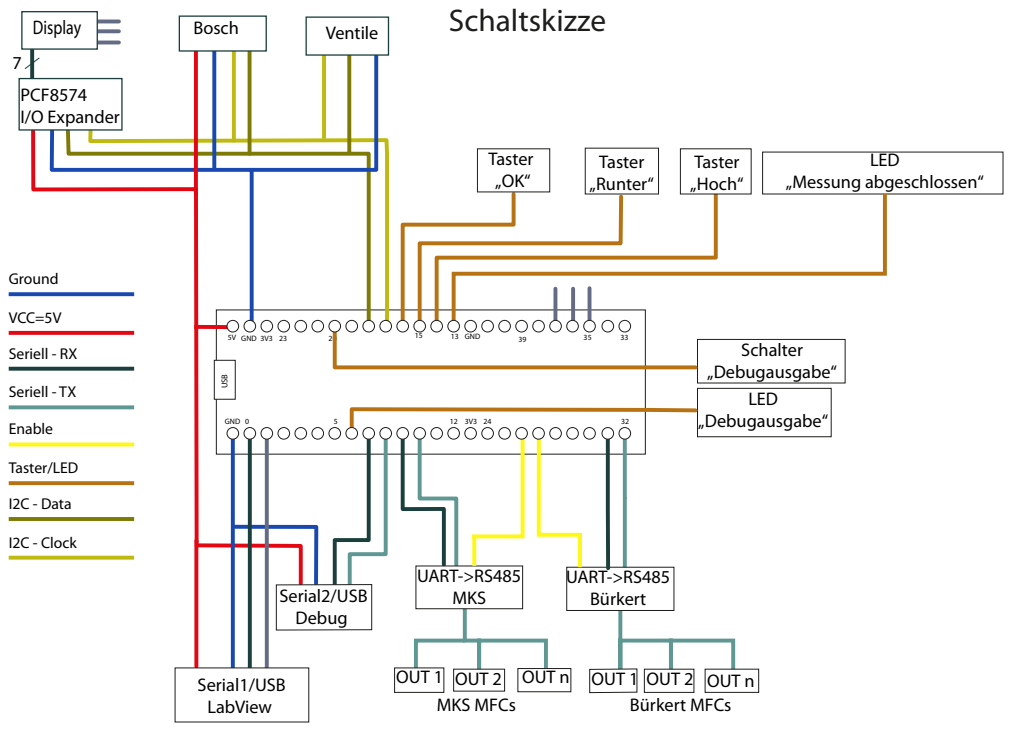
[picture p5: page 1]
GND; UART->RS485 Bürkert; UART->RS485 MKS; Serial1/USB LabView; Serial2/USB Debug; USB; LED „Messung abgeschlossen“; Schalter „Debugausgabe“ LED; „Debugausgabe“; 35 GND 3V3 23; 13 GND; PCF8574 I/O Expander; Taster „OK“; Taster „Runter“; Taster „Hoch“; Display; Bosch; Ventile; Ground; VCC=5V; Seriell - RX; Seriell - TX; Enable; Taster/LED; I2C - Data; I2C - Clock

OUT 1 OUT 2 OUT n
MKS MFCs

Bürkert MFCs

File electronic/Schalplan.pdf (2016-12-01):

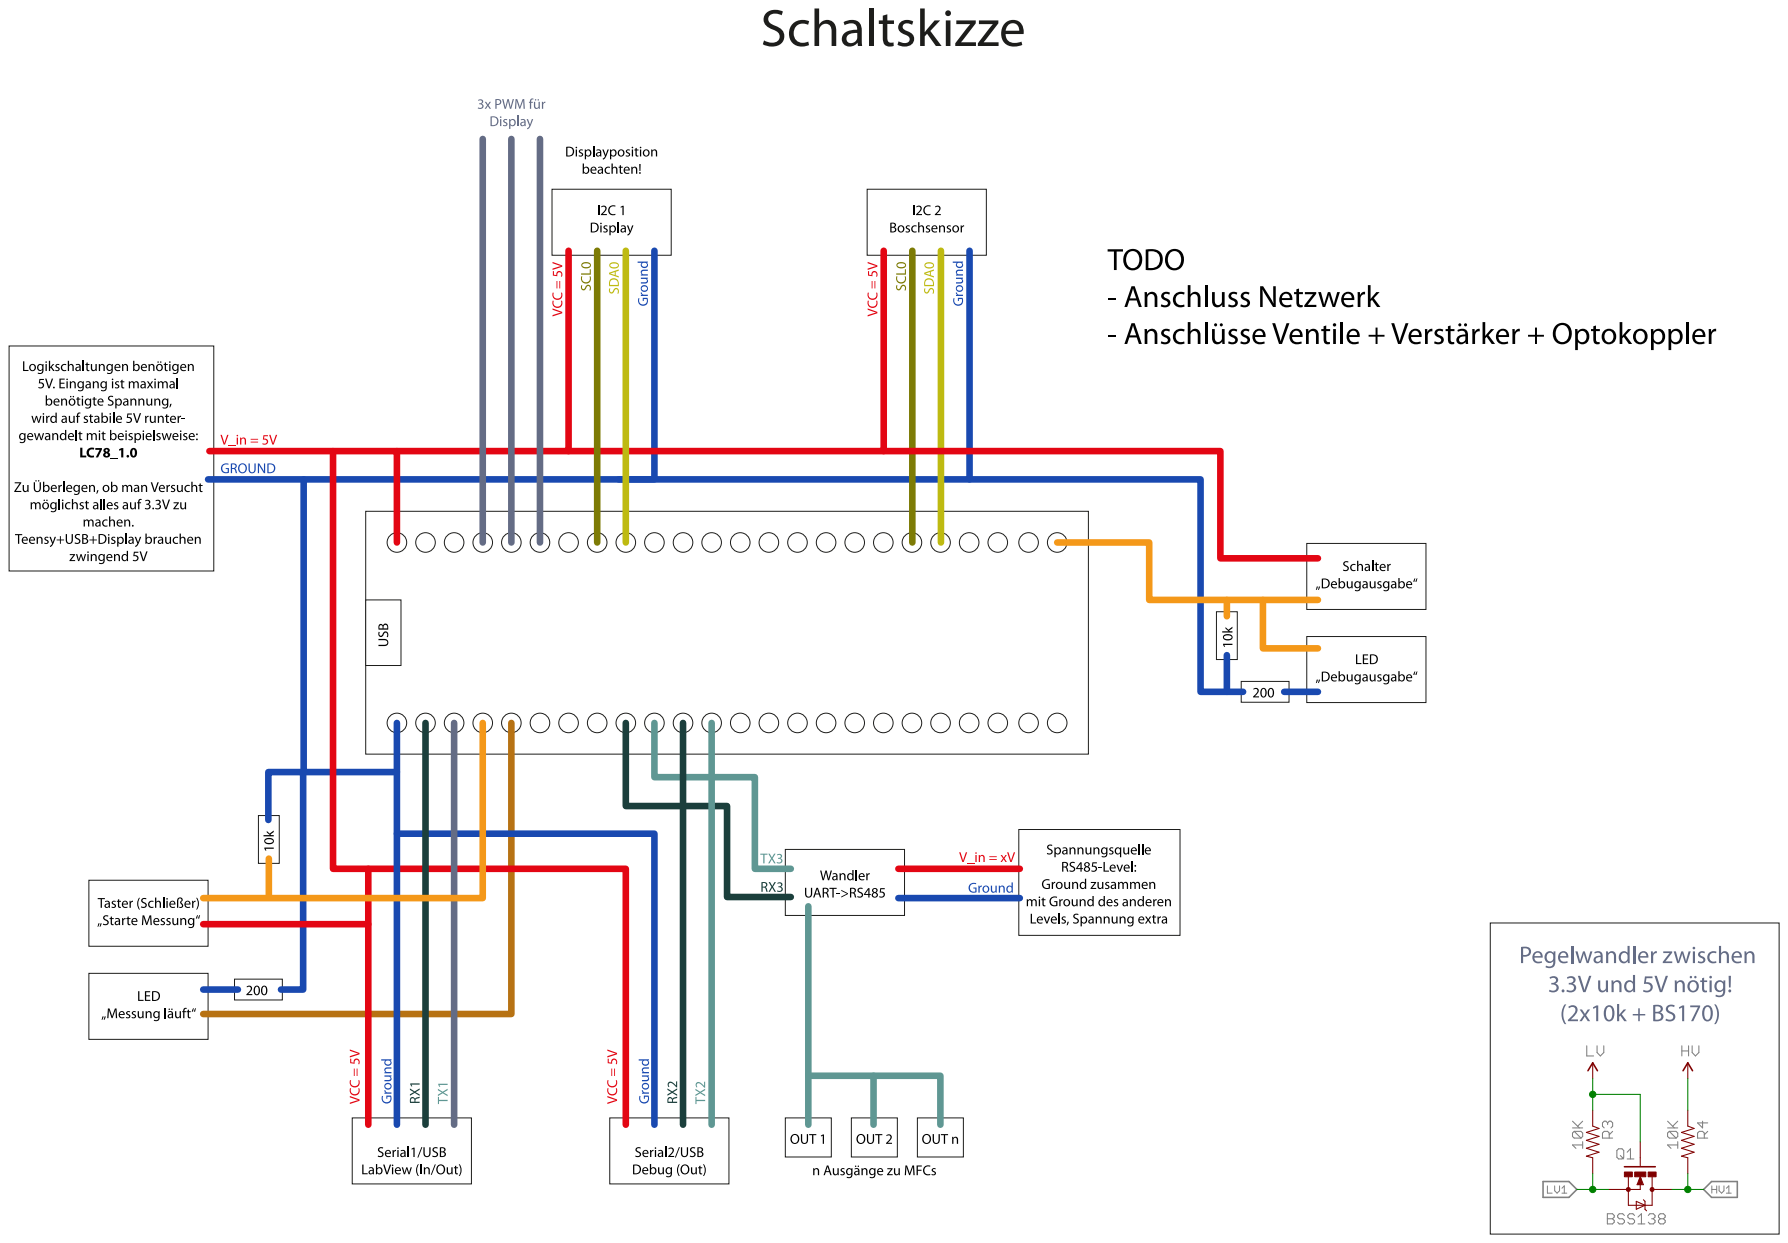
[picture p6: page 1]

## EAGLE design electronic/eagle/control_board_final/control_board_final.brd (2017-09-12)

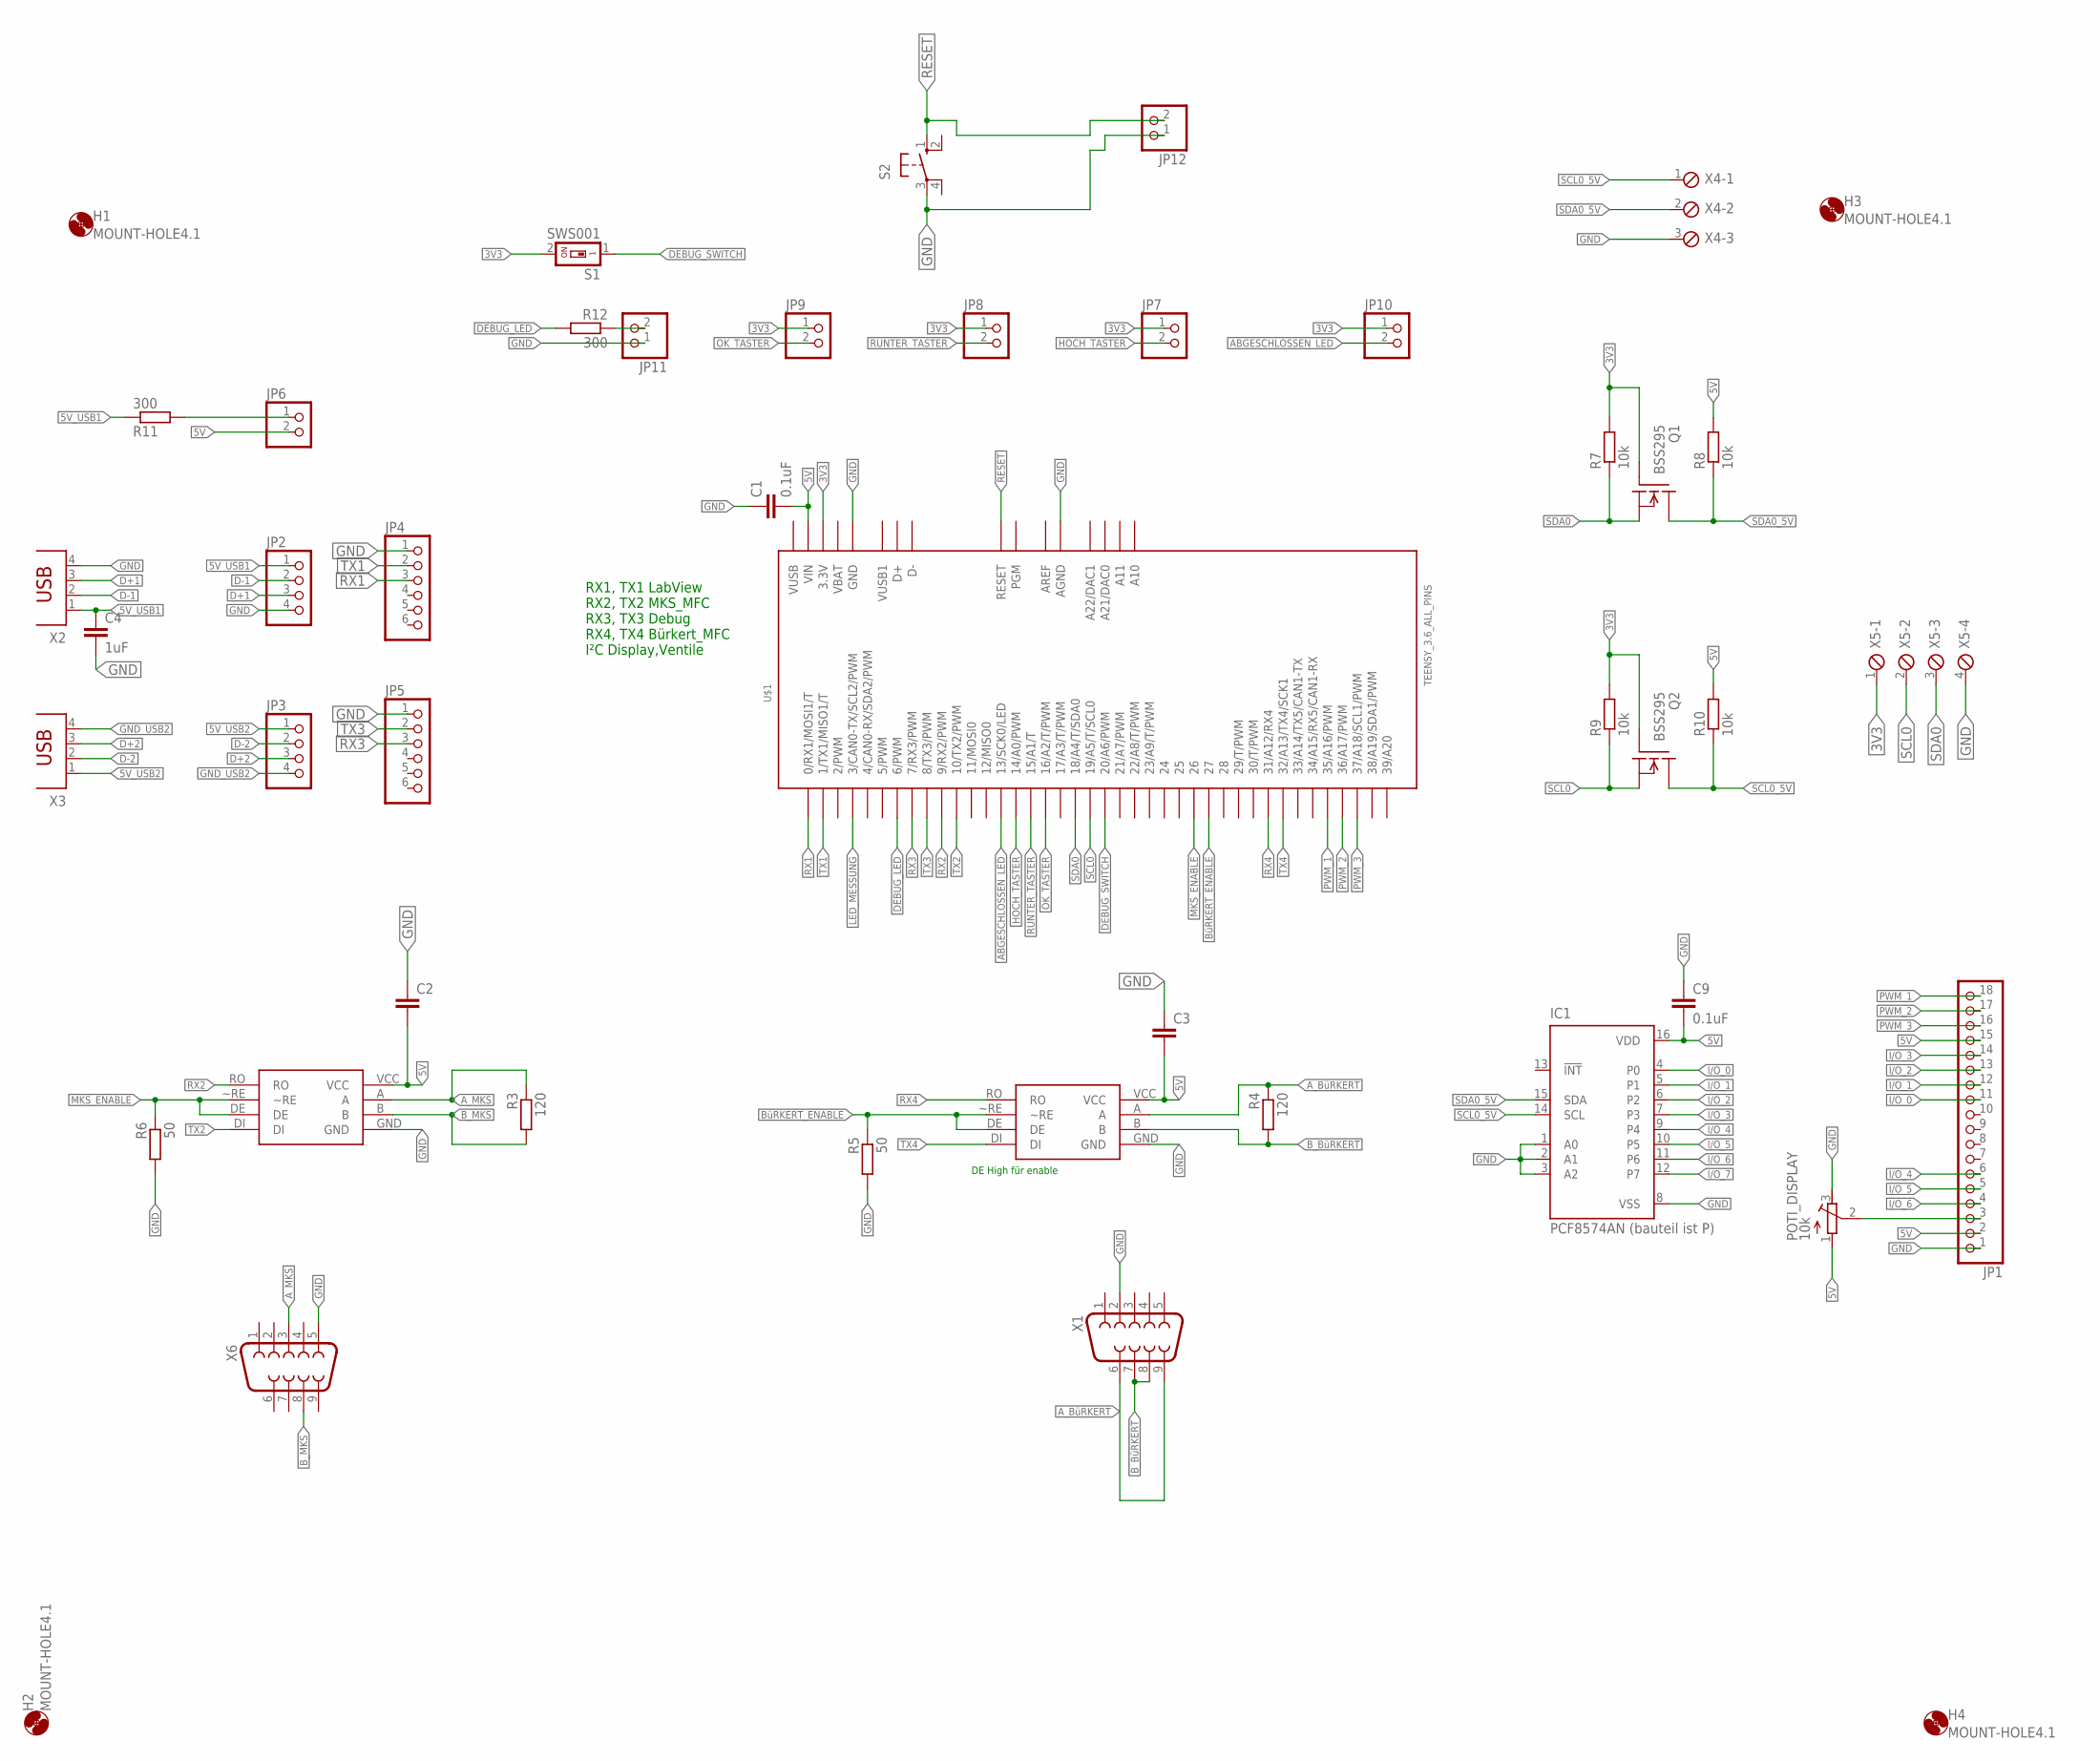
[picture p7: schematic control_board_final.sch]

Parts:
C1, C9: 0.1uF; C0805
C2, C3: C-EUC0805; C0805
C4: 1uF; C0805
H1, H2, H3, H4: MOUNT-HOLE4.1; 4,1
IC1: PCF8574AN (bauteil ist P); DIL16
JP1: PINHD-1X18; 1X18
JP2, JP3: PINHD-1X4; 1X04
JP4, JP5: PINHD-1X6; 1X06
JP6, JP7, JP8, JP9, JP10, JP11, JP12: PINHD-1X2; 1X02
POTI_DISPLAY: 10k; RTRIM3374
Q1, Q2: BSS295; TO92
R3, R4: 120; R0805
R5, R6: 50; R0805
R7, R8, R9, R10: 10k; VMTA55
R11, R12: 300; R0805
S1: SWS001; SMS-001
S2: 10-XX; B3F-10XX
U$1: TEENSY_3.6_ALL_PINS
U$5, U$6: MAX14775EASA+; SO08
X1, X6: F09HP
X2, X3: PN61729
X4: MPT3; 3POL254
X5: MPT4; 4POL254

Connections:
3V3: JP7.1, JP8.1, JP9.1, JP10.1, Q1.1 (G), Q2.1 (G), R7.2, R9.2, S1.2, U$1.3.3V, U$1.3.3V3 (3.3V), U$1.3.3V4 (3.3V), X5.1
5V: C1.2, C2.2, C3.2, C9.2, IC1.16 (VDD), JP1.2, JP1.15, JP6.2, POTI_DISPLAY.1 (A), R8.2, R10.2, U$1.VIN, U$5.VCC, U$6.VCC
5V_USB1: C4.1, JP2.1, R11.1, X2.1
5V_USB2: JP3.1, X3.1
ABGESCHLOSSEN_LED: JP10.2, U$1.13 (13/SCK0/LED)
AREF: U$1.AREF
A_BüRKERT: R4.1, U$5.A, X1.6, X1.9
A_MKS: R3.1, U$6.A, X6.3
B_BüRKERT: R4.2, U$5.B, X1.7, X1.8
B_MKS: R3.2, U$6.B, X6.8
BüRKERT_ENABLE: R5.1, U$1.27, U$5.DE, U$5.~RE
D+1: JP2.3, X2.3
D+2: JP3.3, X3.3
D-1: JP2.2, X2.2
D-2: JP3.2, X3.2
DEBUG_LED: R12.2, U$1.6 (6/PWM)
DEBUG_SWITCH: S1.1, U$1.20/A6 (20/A6/PWM)
GND: C1.1, C2.1, C3.1, C4.2, C9.1, IC1.1 (A0), IC1.2 (A1), IC1.3 (A2), IC1.8 (VSS), JP1.1, JP2.4, JP4.1, JP5.1, JP11.1, JP12.1, POTI_DISPLAY.3 (E), R5.2, R6.2, S2.3, U$1.AGND, U$1.GND, U$1.GND1 (GND), U$1.GND3 (GND), U$1.GND4 (GND), U$1.GND6 (GND), U$5.GND, U$6.GND, X1.2, X2.4, X4.3, X5.4, X6.5
GND_USB2: JP3.4, X3.4
HOCH_TASTER: JP7.2, U$1.14/A0 (14/A0/PWM)
I/O_0: IC1.4 (P0), JP1.11
I/O_1: IC1.5 (P1), JP1.12
I/O_2: IC1.6 (P2), JP1.13
I/O_3: IC1.7 (P3), JP1.14
I/O_4: IC1.9 (P4), JP1.6
I/O_5: IC1.10 (P5), JP1.5
I/O_6: IC1.11 (P6), JP1.4
I/O_7: IC1.12 (P7)
LED_MESSUNG: U$1.3 (3/CAN0-TX/SCL2/PWM)
MKS_ENABLE: R6.1, U$1.26, U$6.DE, U$6.~RE
unnamed: JP6.1, R11.2
unnamed: JP11.2, R12.1
OK_TASTER: JP9.2, U$1.16/A2 (16/A2/T/PWM)
POTI: JP1.3, POTI_DISPLAY.2 (S)
PWM_1: JP1.18, U$1.35/A16 (35/A16/PWM)
PWM_2: JP1.17, U$1.36/A17 (36/A17/PWM)
PWM_3: JP1.16, U$1.37/A18 (37/A18/SCL1/PWM)
RESET: JP12.2, S2.1 (S), U$1.RESET
RUNTER_TASTER: JP8.2, U$1.15/A1 (15/A1/T)
RX1: JP4.3, U$1.0 (0/RX1/MOSI1/T)
RX2: U$1.9 (9/RX2/PWM), U$6.RO
RX3: JP5.3, U$1.7 (7/RX3/PWM)
RX4: U$1.31/A12 (31/A12/RX4), U$5.RO
SCL0: Q2.3 (S), R9.1, U$1.19/A5 (19/A5/T/SCL0), X5.2
SCL0_5V: IC1.14 (SCL), Q2.2 (D), R10.1, X4.1
SDA0: Q1.3 (S), R7.1, U$1.18/A4 (18/A4/T/SDA0), X5.3
SDA0_5V: IC1.15 (SDA), Q1.2 (D), R8.1, X4.2
TX1: JP4.2, U$1.1 (1/TX1/MISO1/T)
TX2: U$1.10 (10/TX2/PWM), U$6.DI
TX3: JP5.2, U$1.8 (8/TX3/PWM)
TX4: U$1.32/A13 (32/A13/TX4/SCK1), U$5.DI
VBAT: U$1.VBAT
VUSB: U$1.VUSB
VUSB1: U$1.VUSB1

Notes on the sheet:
RX1, TX1 LabView RX2, TX2 MKS_MFC RX3, TX3 Debug RX4, TX4 Bürkert_MFC I²C Display,Ventile
DE High für enable

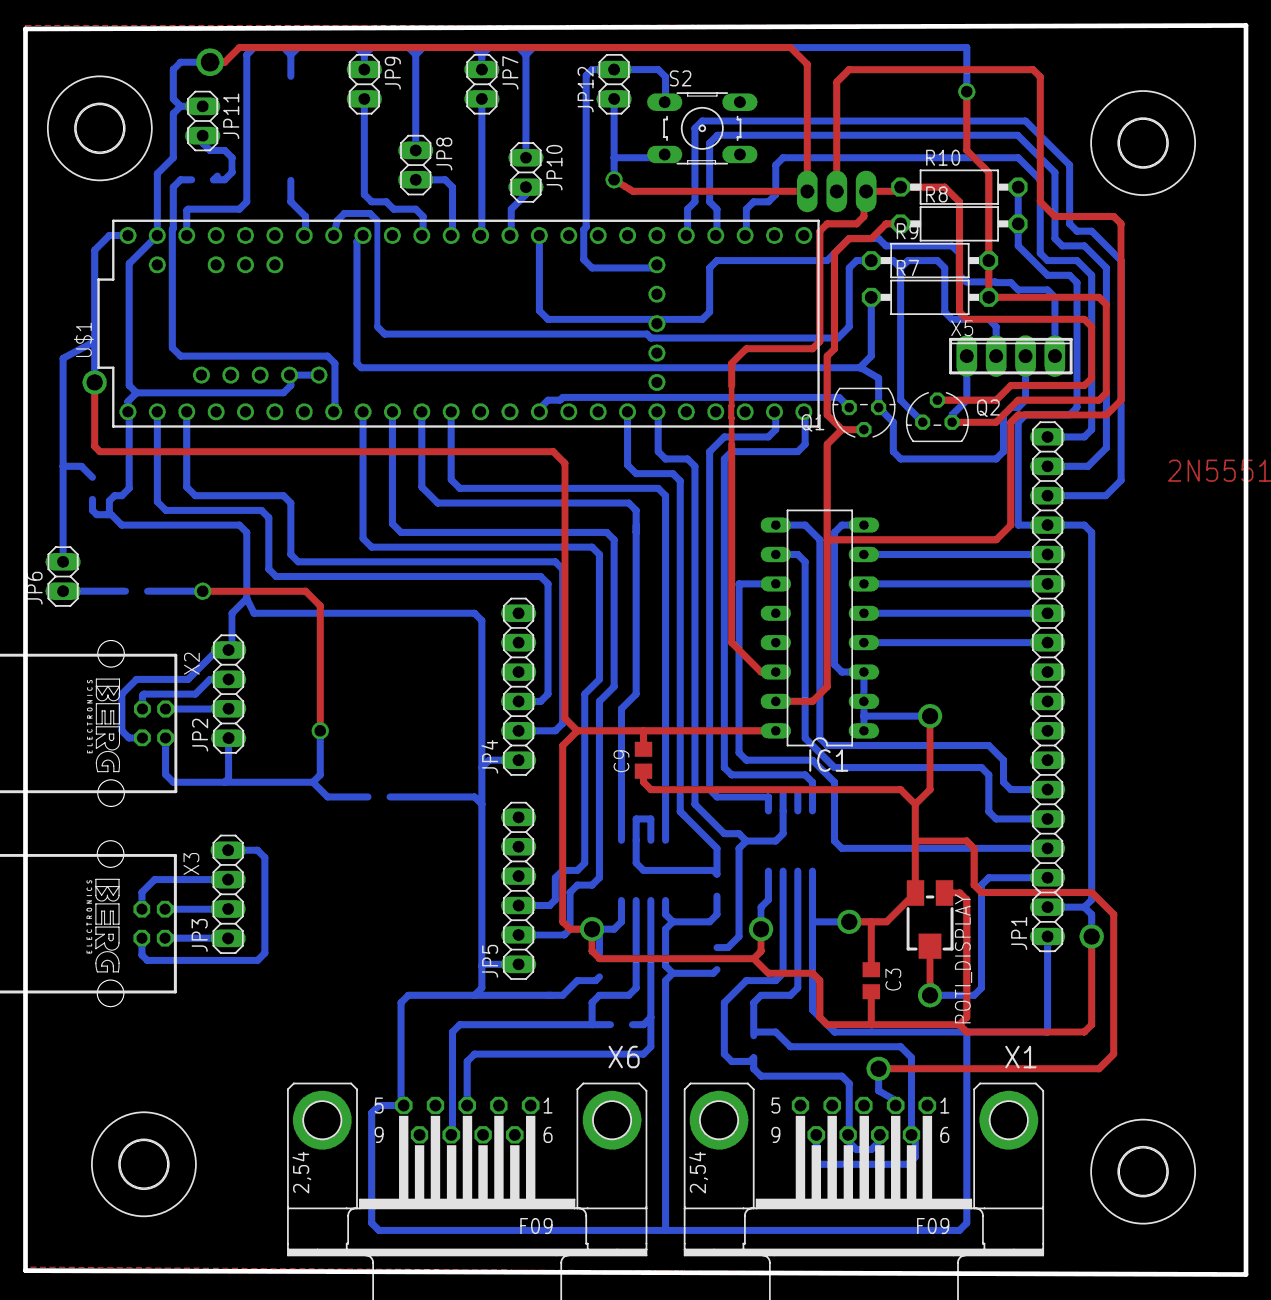
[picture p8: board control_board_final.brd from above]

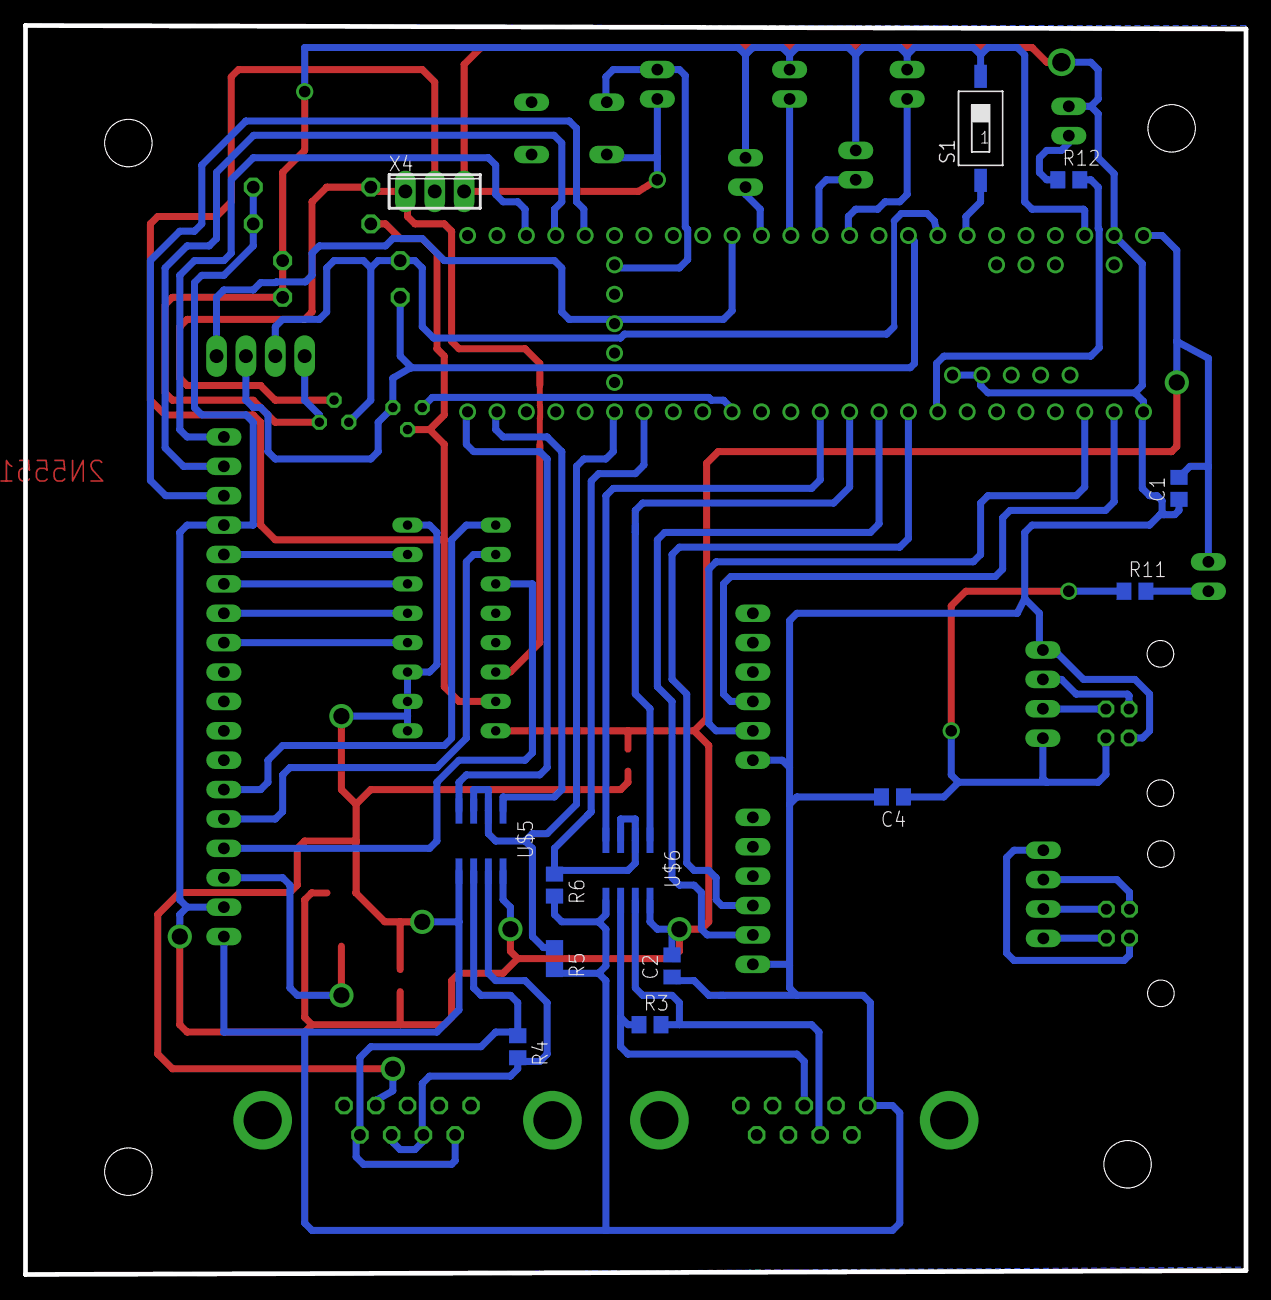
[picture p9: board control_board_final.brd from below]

Board: 2 copper layers, 105.5 x 108.0 mm, 46 parts (13 on the bottom side), 48 nets.

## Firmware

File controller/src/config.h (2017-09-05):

#ifndef CONFIG_H
#define CONFIG_H

// In dieser Datei werden Hardgecodete Einstellungen vorgenommen

//SERIAL BAUDRATES
#define SERIAL_LABVIEW_BAUDRATE 115200
#define SERIAL_DEBUG_BAUDRATE 115200
#define SERIAL_MKS_BAUDRATE 115200
#define SERIAL_BUERKERT_BAUDRATE 9600

//SERIAL READ CONFIGS
#define SERIAL_READ_TIMEOUT 1000 //Zeit in ms, die eine Zeilenuebertragung maximal beanspruchen darf
#define SERIAL_READ_MAX_LINE_SIZE 512 //Maximale Laenge einer uebertragenenen Zeile
#define SERIAL_READ_MAX_BLOCK_SIZE 16 //Maximale Laenge eines Eintrages (Zerlegter Uebertragungsstring)
#define SERIAL_READ_MAX_BLOCK_AMOUNT 64 //Maximale Anzahl an Eintraegen pro Zeile

//SD CONFIGS
#define SDCARD_READ_TIMEOUT 250 //Zeit in ms, die eine Zeile maximal zum Einlesen brauchen darf

//OBJECTSIZE
#define MAX_AMOUNT_MFC 32
#define MAX_AMOUNT_VALVE 32
#define MAX_AMOUNT_VALVE_PCB 8

//DISPLAY CONFIGS
#define DISPLAY_SIZE_WIDTH 20 //Anzahl der horizontalen Chars
#define DISPLAY_SIZE_HEIGHT 4 //Anzahl der vertikalen Chars
#define DISPLAY_REDRAW_INTERVALL 50 //ms, Bestimmt Häufigkeit der Bildaktualisierung, Errors ausgenommen
#define PIN_DISPLAY_RED 37 //pwm
#define PIN_DISPLAY_GREEN 36 //pwm
#define PIN_DISPLAY_BLUE 35 //pwm

//MENU AND BUTTONS
#define MENU_MAX_AMOUNT_ENTRIES 64 //maximale Anzahl an Programmen, die dargestellt werden können
#define INPUTS_MAX_AMOUNT_BUTTONS 8 //maximale Anzahl an Tastern, die ausgelesen werden können

//INPUT OUTUT
#define PIN_DEBUGSWITCH 20 //input
#define PIN_OKBUTTON 16 //input
#define PIN_DOWNBUTTON 15 //input
#define PIN_UPBUTTON 14 //input
#define PIN_DEBUGLED 6 //output
#define PIN_FINISHLED 13 //output

#define PIN_ENABLE_MKS 26 //output
#define PIN_ENABLE_BUERKERT 27 //output

#define PIN_SOFTWARE_RESET 23 //output

//MFC COMMUNICATION TIMINGS
#define MKS_READ_START_TIME 400 //microseconds
#define MKS_ANSWER_TIMEOUT 5 //milliseconds
#define MKS_READ_TIMEOUT 5 //milliseconds

#define BUERKERT_READ_START_TIME 1000 //microseconds
#define BUERKERT_ANSWER_TIMEOUT 25 //milliseconds
#define BUERKERT_READ_TIMEOUT 25 //milliseconds

#define MFC_READ_TIMING 250 //ms, Zeitintervall, in dem die MFC Ist-Werte nacheinander ausgelesen werden (10 MFCs = 2,5s für einen Zyklus)

//ADDRESSES
#define ADDRESS_I2C_BOSCH 0x76
#define ADDRESS_I2C_DISPLAY 0x38

//ERORRORCODES
#define ERR_SERIAL_READ_MAX_STRING_SIZE 1000
#define ERR_SERIAL_READ_WRONG_LINE_BEGIN 1001
#define ERR_SERIAL_READ_WRONG_LINE_ENDING 1002
#define ERR_SERIAL_READ_TIMEOUT 1003
#define ERR_SERIAL_COMMANDS_WRONG_AMOUNT 1004
#define ERR_SERIAL_UNDEFINED_INDEX 5000

//Anzeigedauer von Fehlern
#define ERR_1000_TIME 1500
#define ERR_5000_TIME 604800000 //1 Woche

#endif

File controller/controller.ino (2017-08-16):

// Dies ist die Hauptdatei unseres Prpgramms. Der Name muss identisch zum Programmverzeichnis sein.
// Hier werden alle Bibliotheken importiert, Threads gestartet und verwaltet

// INCLUDES
#include <newdel.h> //fügt new und delete hinzu, wird für "mthread" benötigt
#include <mthread.h>
#include <QueueList.h>
#include <Wire.h>

//Klassen aus Includes mit einem "main" im Namen werden in dieser Datei erstellt
//und haben einen Thread
#include "src/main_labCom.h"
#include "src/main_mfcCtrl.h"
#include "src/main_valveCtrl.h"
#include "src/main_boschCom.h"
#include "src/main_display.h"
#include "src/main_stringBuilder.h"
#include "src/StoreD.h"
#include "src/mfcCtrl.h"
#include "src/valveCtrl.h"
#include "src/parseInput.h"

#include "src/ownlibs/serialCommunication.h"
#include "src/ownlibs/inputHandler.h"

//OBJEKTVARIABLEN ERSTELLEN
io::Main_Display *main_display;
io::InputHandler *inputHandler;
communication::Main_LabCom *main_labCom;
communication::Main_BoschCom *main_boschCom;
communication::Main_StringBuilder *main_stringBuilder;
communication::ParseInput *parseInput;
control::Main_MfcCtrl *main_mfcCtrl;
control::Main_ValveCtrl *main_valveCtrl;
storage::StoreD *storeD;

void debug(uint8_t value) {
  //set debug-status to srl
  srl->activateDebug(value);
  digitalWrite(PIN_DEBUGLED, value);
}

void ok_start(uint8_t value) {
  //die beiden Funktionen sind niemals zur gleichen Zeit "gueltig",
  //das ueberpruefen sie aber selber beim Aufruf.
  main_labCom->start();
  main_display->menu_controlMenu();
}

void button_up(uint8_t value) {
  main_display->menu_navigateMenu(0);
}

void button_down(uint8_t value) {
  main_display->menu_navigateMenu(1);
}

uint16_t parseNewLine_withoutClass(char newLine[]) {
  return parseInput->parseNewLine(newLine);
}

void readFile_withoutClass(char name[]) {
  storeD->readFile(name);
}

void start_withoutClass() {
  main_labCom->start();
}

void setLaodingProgress_withoutClass(int8_t loadingProgress) {
  main_display->setLaodingProgress(loadingProgress);
}

void setup() {
  // ERSTELLE SERIELLE VERBINDUNGEN
  srl->setSerial(&Serial1, &Serial3, &Serial2, &Serial4); //labview / debug / mks / buerkert

  // ERSTELLE GEBRAUCHTE OBJEKTE
  main_display       = new io::Main_Display();
  inputHandler       = new io::InputHandler();
  main_labCom        = new communication::Main_LabCom();
  main_boschCom      = new communication::Main_BoschCom();
  main_stringBuilder = new communication::Main_StringBuilder();
  parseInput         = new communication::ParseInput();
  main_mfcCtrl       = new control::Main_MfcCtrl();
  main_valveCtrl     = new control::Main_ValveCtrl();
  storeD             = new storage::StoreD(); //stringBuilder, this

  // TAUSCHE OBJEKTPOINTER ZWISCHEN OBJEKTEN AUS
  main_labCom->setMainMfcObjectPointer(main_mfcCtrl);
  main_labCom->setMainValveObjectPointer(main_valveCtrl);
  main_labCom->setMainBoschObjectPointer(main_boschCom);
  main_labCom->setMainDisplayObjectPointer(main_display);
  main_labCom->setMainStringBuilderObjectPointer(main_stringBuilder);
  main_labCom->setParseInputObjectPointer(parseInput);

  parseInput->setMainMfcObjectPointer(main_mfcCtrl);
  parseInput->setMainValveObjectPointer(main_valveCtrl);
  parseInput->setMainBoschObjectPointer(main_boschCom);
  parseInput->setMainDisplayObjectPointer(main_display);
  parseInput->setMainStringBuilderObjectPointer(main_stringBuilder);

  main_mfcCtrl->setMainDisplayObjectPointer(main_display);

  main_valveCtrl->setMainDisplayObjectPointer(main_display);

  main_stringBuilder->setMainValveObjectPointer(main_valveCtrl);
  main_stringBuilder->setMainMfcObjectPointer(main_mfcCtrl);
  main_stringBuilder->setMainBoschObjectPointer(main_boschCom);
  main_stringBuilder->setStoreDObjectPointer(storeD);

  storeD->setParseInputNewLineFunction(parseNewLine_withoutClass);
  storeD->setLoadingProgressFunction(setLaodingProgress_withoutClass);
  main_display->setReadFileFunction(readFile_withoutClass);
  parseInput->set_startFunction(start_withoutClass);

  // GENERIERE PROGRAMMLISTE
  char programs[32][16];
  int amount = storeD->listsource(programs);
  cmn::sort(programs, amount);
  main_display->menu_setMenuItems(programs, amount);

  // STARTE PSEUDOTHREADS
  main_thread_list -> add_thread(main_display);
  main_thread_list -> add_thread(inputHandler);
  main_thread_list -> add_thread(main_labCom);
  main_thread_list -> add_thread(main_boschCom);
  main_thread_list -> add_thread(main_stringBuilder);
  main_thread_list -> add_thread(main_mfcCtrl);
  main_thread_list -> add_thread(main_valveCtrl);

  // INIT LEDS
  pinMode(PIN_DEBUGLED, OUTPUT);
  pinMode(PIN_FINISHLED, OUTPUT);

  // ERSTELLE INTERRUPTS FUER TASTER
  pinMode(PIN_DEBUGSWITCH, INPUT_PULLDOWN);
  pinMode(PIN_OKBUTTON, INPUT_PULLDOWN);
  pinMode(PIN_UPBUTTON, INPUT_PULLDOWN);
  pinMode(PIN_DOWNBUTTON, INPUT_PULLDOWN);
  inputHandler->addInterrupt(PIN_DEBUGSWITCH, debug, CHANGE);
  inputHandler->addInterrupt(PIN_OKBUTTON, ok_start, RISING);
  inputHandler->addInterrupt(PIN_UPBUTTON, button_up, RISING, 350, 75);
  inputHandler->addInterrupt(PIN_DOWNBUTTON, button_down, RISING, 350, 75);

  // INIT SWITCH
  srl->activateDebug(digitalRead(PIN_DEBUGSWITCH));
  digitalWrite(PIN_DEBUGLED, digitalRead(PIN_DEBUGSWITCH));

  // SOFTWARE RESET INIT //TODO
  pinMode(PIN_SOFTWARE_RESET, OUTPUT);

  // INIT ANGESCHOSSEN
  main_display->foundSDcard(storeD->foundSDcard()); //setze SD-Card Flag
  main_display->boardIsReady(); //zeige "Board bereit" an
  srl->println('L', "ready"); //Sende Startbefehl an LabView
}

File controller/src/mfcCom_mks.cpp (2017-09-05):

#include "mfcCom_mks.h"

namespace communication {
    namespace Mks {
        //ohne Objektorientierung muessen Variablen im CPP deklariert werden
        IntervalTimer *eventTimer;
        bool busy;
        uint32_t transmission_startTime;

        float *destination_value_ptr;
        uint8_t estimated_answer_length;
        //ende

        void init() {
            eventTimer = new IntervalTimer();
            busy = false;
            transmission_startTime = 0;
            estimated_answer_length = 0;

            pinMode(PIN_ENABLE_MKS, OUTPUT);
            digitalWrite(PIN_ENABLE_MKS, HIGH);
        }

        bool writeValue(char address[], float value, float *destination) {
            //calculate value string
            char value_string[8];
            uint8_t first_digit = (uint8_t) value;
            uint32_t last_digits = 0;
            if (first_digit < 10) {
                last_digits = (value - first_digit) * 100000;
                sprintf(value_string, "%d.%05lu", first_digit, last_digits);
            } else {
                last_digits = (value - first_digit) * 10000;
                sprintf(value_string, "%d.%04lu", first_digit, last_digits);
            }

            if (_writeCommand(address, 'S', value_string)) {
                destination_value_ptr = destination;
                estimated_answer_length = 8; //TODO
                return true;
            }
            return false;
        }

        bool readValue(char address[], float *destination) {
            if (_writeCommand(address, 'F', (char*) "")) {
                destination_value_ptr = destination;
                estimated_answer_length = 8; //TODO
                return true;
            }
            return false;
        }


        //HELPERFUNKTIONEN

        bool _writeCommand(char address[], char command, char value_string[]) {
            //Wenn Antwort von MFC noch nicht erhalten wurde, dann gebe false zurueck,
            //Befehl muss erneut gesetzt werden (vorheriger Befehl)
            if (busy && millis() - transmission_startTime < MKS_ANSWER_TIMEOUT)
                return false;
            busy = true;
            transmission_startTime = millis();

            digitalWrite(PIN_ENABLE_MKS, HIGH);

            //Berechne Befehlslaenge
            uint8_t command_length = 5; //preambel, address, commandChar, termination
            for (uint8_t i = 0; value_string[i] != '\0'; i++)
                command_length++;

            //berechne Uebertragungszeit (microseconds)
            //Zeit pro Bit         : 1.0 / SERIAL_MKS_BAUDRATE * 1000000
            //Anzahl Bits pro Byte : 10 (start + stop bit)
            //Anzahl Bytes         : command_length
            uint32_t transmission_time = 1.0 / (double) SERIAL_MKS_BAUDRATE * 1000000 * 10 * command_length;
            transmission_time += 0.5 * MKS_READ_START_TIME; //Wechsel Modus in Mitte der Uebertragungspause
            eventTimer->begin(_writeCommand_changeEnable, transmission_time);

            srl->print('M', "@");
            srl->print('M', address);
            srl->print('M', command); //Setze Fluss
            srl->print('M', value_string);
            srl->print('M', '\r'); //Termimierung

            return true;
        }

        void _writeCommand_changeEnable() {
            eventTimer->end(); //Timer soll nur einmal ausgefuehrt werden
            digitalWrite(PIN_ENABLE_MKS, LOW); //schalte in Lesemodus

            //berechne Uebertragungszeit (microseconds)
            //Zeit pro Bit         : 1.0 / SERIAL_MKS_BAUDRATE * 1000000
            //Anzahl Bits pro Byte : 10 (start + stop bit)
            //Anzahl Bytes         : estimated_answer_length
            uint32_t transmission_time = 1.0 / (double) SERIAL_MKS_BAUDRATE * 1000000 * 10 * estimated_answer_length;
            transmission_time += 0.5 * MKS_READ_START_TIME;
            eventTimer->begin(_writeCommand_readAnswer, transmission_time);
        }

        void _writeCommand_readAnswer() {
            //Lesen nachdem Serielle Uebertragung der Antwort abgeschlossen ist
            eventTimer->end(); //Timer soll nur einmal ausgefuehrt werden
            busy = false; //COM Modul ist nach Abarbeitung dieses Auftrags wieder fuer neue Befehle bereit

            uint8_t charId = 0;
            uint32_t read_startTime = millis();
            char response[16];
            while (millis() - read_startTime < MKS_READ_TIMEOUT) {
                 //warte, wenn gerade kein Zeichen in Buffer, aber String nicht abgeschlossen
                if (srl->available('M') <= 0)
                    continue;
                char newChar = srl->read('M');
                if (newChar == '\r') { //string abgeschlossen
                    response[charId] = '\0';
                    break;
                }
                response[charId] = newChar;
                charId++;
            }
            digitalWrite(PIN_ENABLE_MKS, HIGH); //setze Pin wieder HIGH, damit writeEnable aktiviert ist

            if (response[0] == '@' && response[1] == '-') {
                char response_new[16];
                uint8_t i = 4;
                for (i; response[i] != '\0'; i++) {
                    response_new[i-4] = response[i];
                }
                response_new[i-4] = '\0';

                *destination_value_ptr = cmn::charArrayToFloat(response_new);
            } else {
                *destination_value_ptr = 0.0;
                srl->println('D', "MFC Antwortet inkorrekt.");
            }
        }
    }
}

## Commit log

2016-11-18 Initialer Commit mit der Dateistruktur
2016-11-21 New file structure, empty ino as arduino-main, node as program main
2016-11-22 1. Funktionierende Dateistruktur, die sich für das Arduino-Board kompilieren lässt
2016-11-23 Threads implementiert, funktionieren nun. Jede Klasse hat ihre eigene loop()-Funktion. Als Haupdatei dient nun wieder die *.ino-Datei
2016-11-26 mfcCtrl: erste in der Theorie funktionierende Steuerung fertiggestellt
2016-11-27 LabCom weiter geführt, Objekte und Threads für die MFCs werden nun in LabCom erstellt. Jedoch hängt sich das Board bei der Ausfuehrung noch immer auf...
2016-11-27 Bug gefixed, Scheint so, als seien maximal 10 Threads möglich
2016-11-29 Overflow-Bug gefixed (unsigned long gilt nun für 49,7 Tage) LabCom Code vereinfacht LabCom verarbeitet nun die komplette Eingabe: Header+EventList MFC-Event-Steuerung steht soweit
2016-12-03 neue serialCommunication Klasse ValveCom "fertig" SwitchCase Struktur eingebaut Bugs fixed: Bug1 MFC-Spam/Abstürze / Bug2 0 und 1 Event pro Objekt führt nicht mehr zu Abstürzen
2016-12-13 Display Bug gefixt, stürzt nicht mehr ab und zeigt richtige Daten an. Dokumentation aktualisiert
2016-12-16 DISPLAY UND KOMMUNIKATIONSUPDATE - RGB-LCD-Display wird unterstützt (Angepasste I2C_LCD Bibliothek wird hierfür verwendet) - Leere Eingabestrings (nur '\n') werden ignoriert - Fehlermeldungen werden 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
2017-01-05 Teensyanpassung begonnen
2017-01-06 Platzhalter Klassen für StringBuilder und BoschCom eingegliedert, Austausch der Pointer, setzen der Initialisierungswerte Bug fixes Readme aktualisiert
2017-01-07 ZWISCHENUPDATE - main_labCom, main_valveCtrl, main_mfcCtrl enthalten nun die gebrauchten Funktionen für den String Builder - Threads von main_valveCtrl und main_mfcCtrl beenden sich nun automatisch n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
2017-01-12 Eagle ergänzt
    [board_projektpraktikum.brd, schematic_projektpraktikum.sch]
2017-01-13 Version 2 des Schaltplans
2017-01-13 Schematic aufgeräumt
    [bord_projektpraktikum_v2.brd, schematic_projektpraktikum_v2.sch, schematic_projektpraktikum_v3.sch]
2017-01-15 Debugging von Main_StringBuilder, Hinzufügen des Kopfs einer Datei (Datum, Messintervall, Anzahl..) in StoreD
2017-02-02 Anpassungen von StringBuilder + Display leuchtet nun gruen nach Fertigstellung der Eventlisten
    [board_projektpraktikum.brd, bord_projektpraktikum_v2.brd, schematic_projektpraktikum_v2.sch, schematic_projektpraktikum_v3.sch]
2017-02-07 Queue List fertig, wird nun auch an String Builder gesendet -> schliesst Datei / kleine Anpassungen / Datumsplatzhalter fuer Header /// noch nicht getestet
2017-02-09 attachInterrupt() hinzugefügt
2017-03-01 Erstellen eines Header in der txt-Datei beim öffnen dieser. Abänderungen an integerToByte.
2017-03-01 alle nach der Änderung aufgetretenen Fehlermeldungen behoben
2017-03-02 kleine Änderung an integerToByte, StoreD und main_stringBuilder
2017-05-27 BME UPDATE - bme Bibliothek von Adafruit rausgesucht und etwas umgeschrieben, Sensor lässt sich nun ansprechen - srl Klasse um "read(constchar type)" und "available(const char type)" erweitert. Somit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
2017-05-28 PCA9555 Eigene Bibliothek zur Ansteuerung des PCA9555 via I2C geschrieben (Test mit Hardware steht noch aus)
2017-05-28 REFACTORING - int, long, ... durch uint8_t, uint16_t, uint32_t ersetzt (und ohne unsigned) - Ventilplatine nun auch in Steuerung komplett eingebunden - Bugs gefixt (und hoffentlich keine neuen eingeb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
2017-05-30 CRASH GEFIXT - zufällige Abstürze des Programmes sind nun behoben - LEDs + Taster implementiert, srl sendet nurnoch Debugnachrichten, wenn Pin 5 HIIGH ist - python script geupdated - kleinere Bugfixe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
2017-06-03 SD-KARTEN-PROGRAMME UND DISPLAYMENÜ - alles etwas umstrukturiert - Menüführung auf dem Display zum Programmstart von der SD Karte - eigene "Interrupt"-Steuerung der Eingangspins (attachInterrupt() sc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
2017-06-04 TESTVERSION MIT VIDEO - vorerst fertige Version mit kleinen Details die noch ausstehen - scheint aktuell Bugfrei
2017-06-09 Code mit StoreD und StringBuilder compiliert nun, ist aber noch zu testen. Programme können nun auch von der SD Karte gelesen werden
2017-06-13 SD UPDATE
    - Programme können nun problemlos von der SD Karte gelesen werden
    - beim Speichern gibt es noch Probleme mit den Strings
2017-06-18 KLEINIGEKEITEN - StoreD speichert nun in Klartext - StoreD speichert nun auch die MFC Typen - StoreD ignoriert nun leere Zeilen beim Lesen aus Textdatei - Boschsensor Werte werden nun (alle drei) auc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
    [board_projektpraktikum.brd, bord_projektpraktikum_v2.brd, control_board_v3.brd, control_board_v3.sch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]
2017-06-18 FILESYSTEM - Dateilisten beim Programmstart sind nun immer korrekt - Scrollen in der Liste ist nun auch bei weniger als drei Einträgen problemlos möglich - Systemdateien, die mit '_' oder '.' beginne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
2017-06-18 FILESYSTEM 2 - Dateinamen werden nun sortiert in Programmauswahl angezeigt - Die beiden Standardordner werden neu erzeugt, falls sie nicht vorhanden sind - es wird eine Beispieldatei im Programmordne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
2017-06-19 SD SYMBOL - kleines Symbol in der linken oberen Ecke zeigt, ob eine SD Karte gefunden wurde
2017-06-23 FINALISIERUNGSUPDATE - I2C Clock läaft nun mit 200kHz, könnte nun bessere Displayperformance geben - Dateileseproblem behoben für Dateien, die mit normalen Char (nicht in Kommentar) enden - SD read T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
2017-07-07 an neue Platine angepasst, Portänderungen + Configerweiterungen, neuer Serieller Port (MKS und Bürkert sind nun getrennt)
2017-07-11 MKS MFC TEST - Mks MFC Ansteuerung geht - Softwarereset - Display mit Ok/Start Knopf während Messung ausschaltbar - MFC Com Objekte funktionieren nun mit flush() und delayMicroseconds (nicht sehr sch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
2017-09-05 DOKU UND MFC - Doku aktualisiert - Labview hinzugefügt - MFCs (MKS) fertig und weitere kleine Änderungen
2017-09-06 Elektronik Teil der readme überarbeitet
2017-09-12 Neue Version des Control-Board
    [control_board_final.brd, control_board_final.sch, control_board_v3.brd, control_board_v3.sch]
